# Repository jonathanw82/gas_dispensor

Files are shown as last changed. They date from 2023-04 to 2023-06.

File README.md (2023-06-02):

<div align="center">
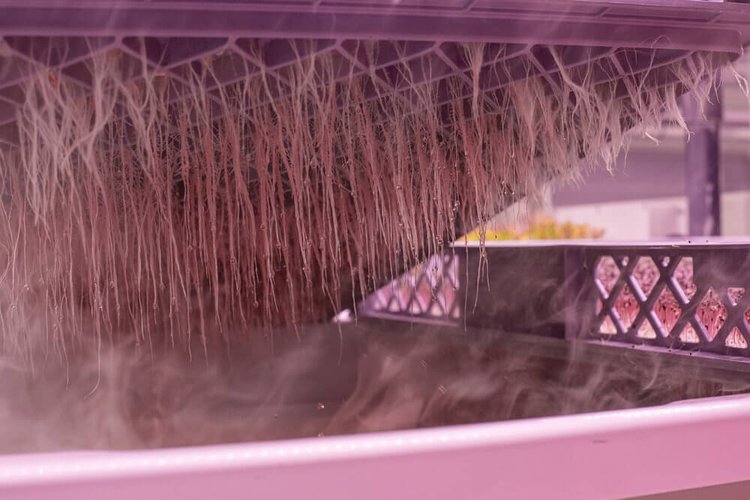
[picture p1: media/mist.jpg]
mist image
   
 </div>

# Overview
This experiment is intended to prove that aeroponics could be less susceptible to [Pythium](https://en.wikipedia.org/wiki/Pythium) a type of root rot, a significant issue for spinach in hydroponic greenhouse production. This test is to confirm that it is possibly due to increased oxygenation with the root zone of the aeroponic system.

The gas dispenser is to reduce the oxygen level in the root zone of an aeroponic growbed by adding nitrogen to bring down the percentage of oxygen.

As can be seen in Fig 1 on average breathable air is made up of oxygen 21%, nitrogen 78.1% and argon and other gasses make only 0.9% of that carbon dioxide makes up 0.04%. 

More information on the composition of air can be found [here.](https://en.wikipedia.org/wiki/Atmosphere_of_Earth)

Therefore increasing the nitrogen level will decrease the oxygen level. Over the growth cycle of some crop this can prove if aeroponics does indeed give the root zone more assess to oxygen and decrease the susceptibility to pythium.

### Fig 1
<div align="center">
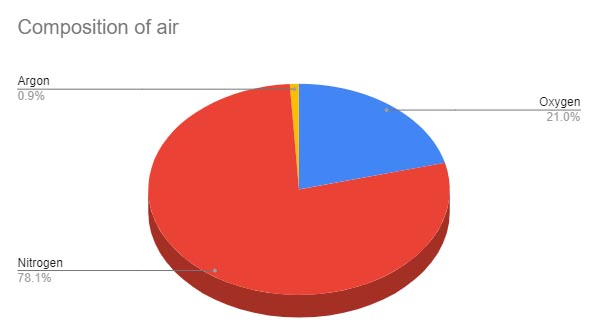
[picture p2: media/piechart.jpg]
piechart
   
 </div>

## Hardware:

* 1 x Arduino Uno wifi rev2
* 1 x Wemos D1 Mini
* 4 x 5v relays
* 1 x 5v PSU
* 1 x Gravity: Electrochemical Oxygen / O2 Sensor (0-100%Vol, I2C) [Here](https://www.dfrobot.com/product-2569.html) (Main 02 sensor) 
* 1 x Gravity: O2 Sensor (Calibrated, I2C & UART) [Here](https://thepihut.com/products/gravity-o2-sensor-calibrated-i2c-uart?variant=41620114866371&currency=GBP&utm_medium=product_sync&utm_source=google&utm_content=sag_organic&utm_campaign=sag_organic&gclid=CjwKCAjw586hBhBrEiwAQYEnHaFBwm7ZAKjgB-vlygECEoYnv8AqbQjYx805CCJuayE0CSrMo6SIVhoCAVIQAvD_BwE) (Safety sensor)
* 1 x Project box
* 5 x Cable glands
* 1 x Cyclinder of nitrogen
* 1 x Bottle regulator with solenoid [Here](https://www.onestopgrowshop.co.uk/pro-leaf-co2-regulator.html)
* 1 x Nitrogen Regulator [Here](https://www.welduk.com/nitrogen-regulator-p64)
* 1 x 1/4 male to 3/8 female BSP adaptor [Here](https://www.air-compressorsdirect.co.uk/bsp-fittings/taper-1-4-male-to-3-8-female-bsp-adaptor)
* 1 x Warning beacon
* 3 x LED's, Red, Green and Amber
* 1 x 4amp 240v MCB
* 1 x 240v to 12v and 5.5v power supply
* 1 x Short piece of din rail 

<br>

| Component               | Consumption        |
| :----------------       | :-----------       |
| Arduino Uno Wifi Rev2   | @ 5v 93 ma         |
| Weemos D1 mini          | @ 5v 70 ma         |
| Twin relay              | @ 5v 40 ma         |
| Single 30amp relay      | @ 5v 20 ma         |
| Oxygen sensor SEN0465   | @ 5v < 5 ma        |
| Oxygen sesnor AA428-210 | @ 5v < 6.5 ma      |
| Warning Beacon          | @ 12v 300 ma       |
| Gas Solenoid            | @ 240v 1 amp       |
| Green status LED        | @ 5v 60 ma         |
| Red status LED          | @ 5v 60 ma         |
| Amber status LED        | @ 5v 60 ma         |
|                         |Total = 1,652.48 amp|

<br>

### Fig 2
<div align="center">
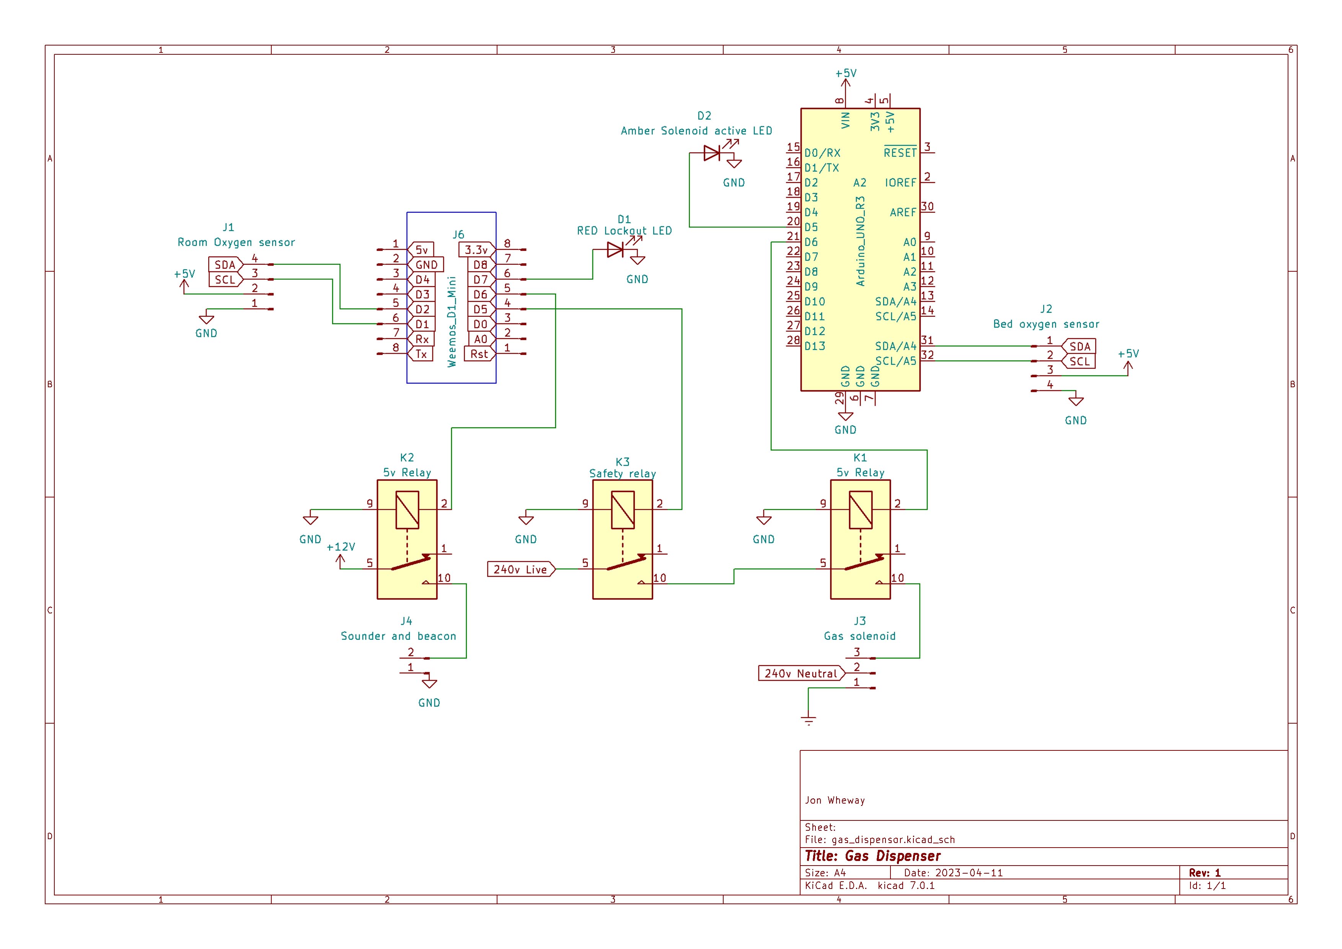
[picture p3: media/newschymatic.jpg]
schymatic
   
 </div>
<br>

## Process:
The safety sensor will read the ambient oxygen level in the room to ascertain if the level of oxygen is within a safe range. Under normal atmospheric pressure conditions, a human normally inhales air that contains 20.9% oxygen, if this falls even by 1 or 2% then it starts to become more laborious and the environment turns hypoxic meaning that oxygen levels are low and could be harmful. [More here](#safety)

If ambient levels are within a safe range the safety relay will energise allowing power throught the dosing relay to energise the solenoid. If 0.0 is reported by the room sensor this is classed as an error. A further 8 samples are taken if they all return 0.0 the error status is reported and the lockout is enguaged and the warning beacon will sound. If during those 8 readings a correct value is retured then the system will continue as normal.

If all is well and the saftey relay is enguaged the bed level oxygen sensor will provide the level of oxygen in the root zone and the dosing solenoid will activate to the specified on off period, lets say 2 seconds on 4 seconds off with a 1 minute pause period to allow the gas to settle and not over shoot the set point. This is also helps to mitigate against the chance of the solenoid from freeing open. This process is repeated to allow more nitrogen into the root zone to bring down the level to the required target. Once the target is met, the system will stop doseing and remain domant until more nitrogen is required and the process starts again. All the while the safety sensor is continuouly checking the oxygen level in the room to keep a safe enviroment.

All the data collected is sent to influxDB for use later, live monitoring can be seen by using mqtt explorer.

### Fig 3
<div align="center">
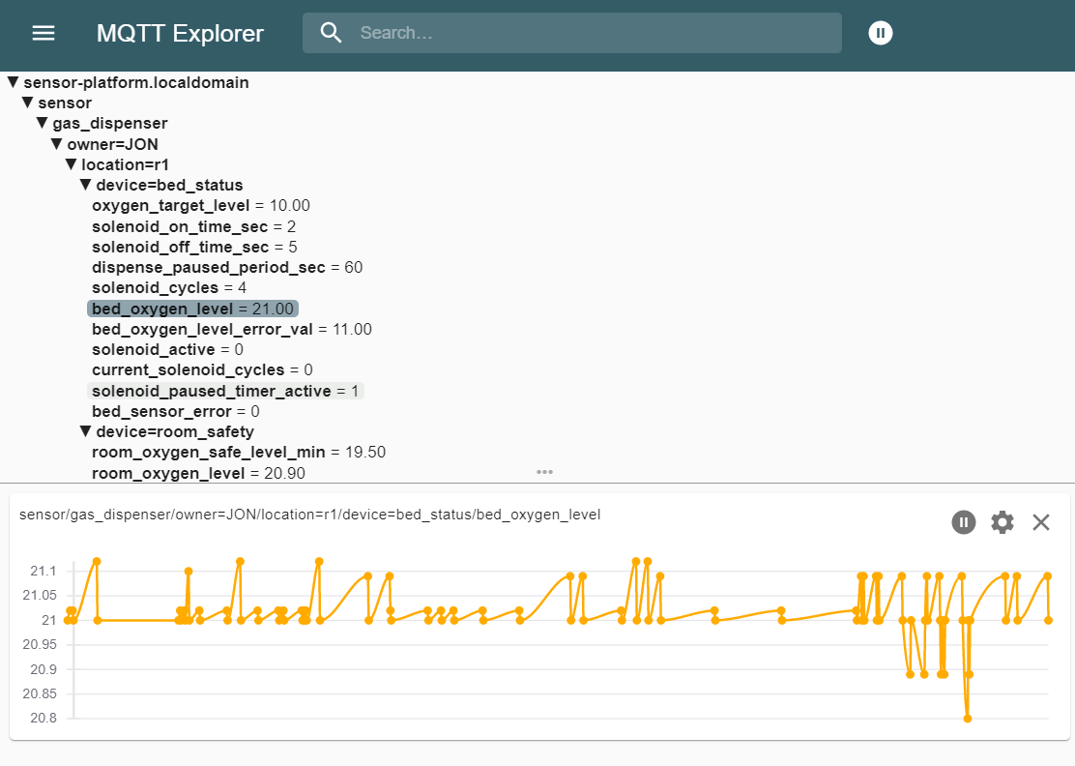
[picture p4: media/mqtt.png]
mqtt
   
 </div>
<br>

## Control commands:
Commands can be sent via mqtt to change certain set points or activate resets.

Sensding this command resets both arduinos.
* gas_dispenser/sub/owner=JON/location=r1/reset

The oxygen target level can be adjusted by sending a number to this command.
* gas_dispenser/sub/owner=JON/location=r1/oxygen_target_level

The solenoid on time can be adjusted by sending a number in seconds.
* gas_dispenser/sub/owner=JON/location=r1/solenoid_on_time_sec

The solenoid off time can be adjusted by sending a number in seconds.
* gas_dispenser/sub/owner=JON/location=r1/solenoid_off_time_sec

The solenoid cycles can be adjusted by sending a number.
* gas_dispenser/sub/owner=JON/location=r1/solenoid_cycles

The solenoid off time can be adjusted by sending a number in seconds.
* gas_dispenser/sub/owner=JON/location=r1/dispense_paused_period_sec

<br>

### Fig 4
<div align="center">
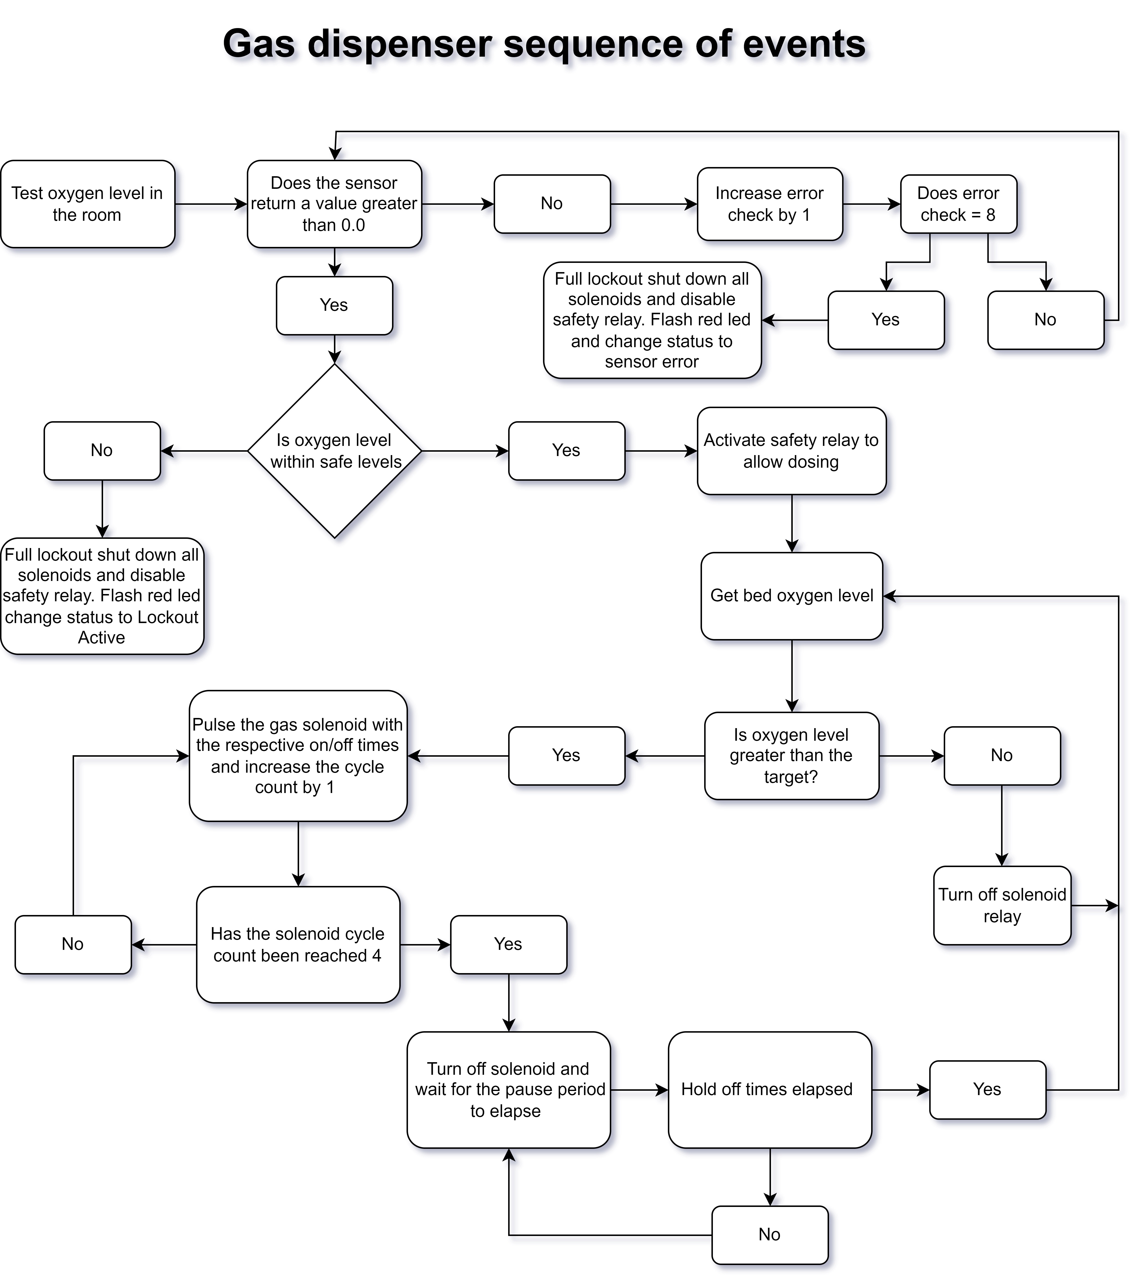
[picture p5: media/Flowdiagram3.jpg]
flowchart3
   
 </div>
<br>

### Fig 5
<div align="center">
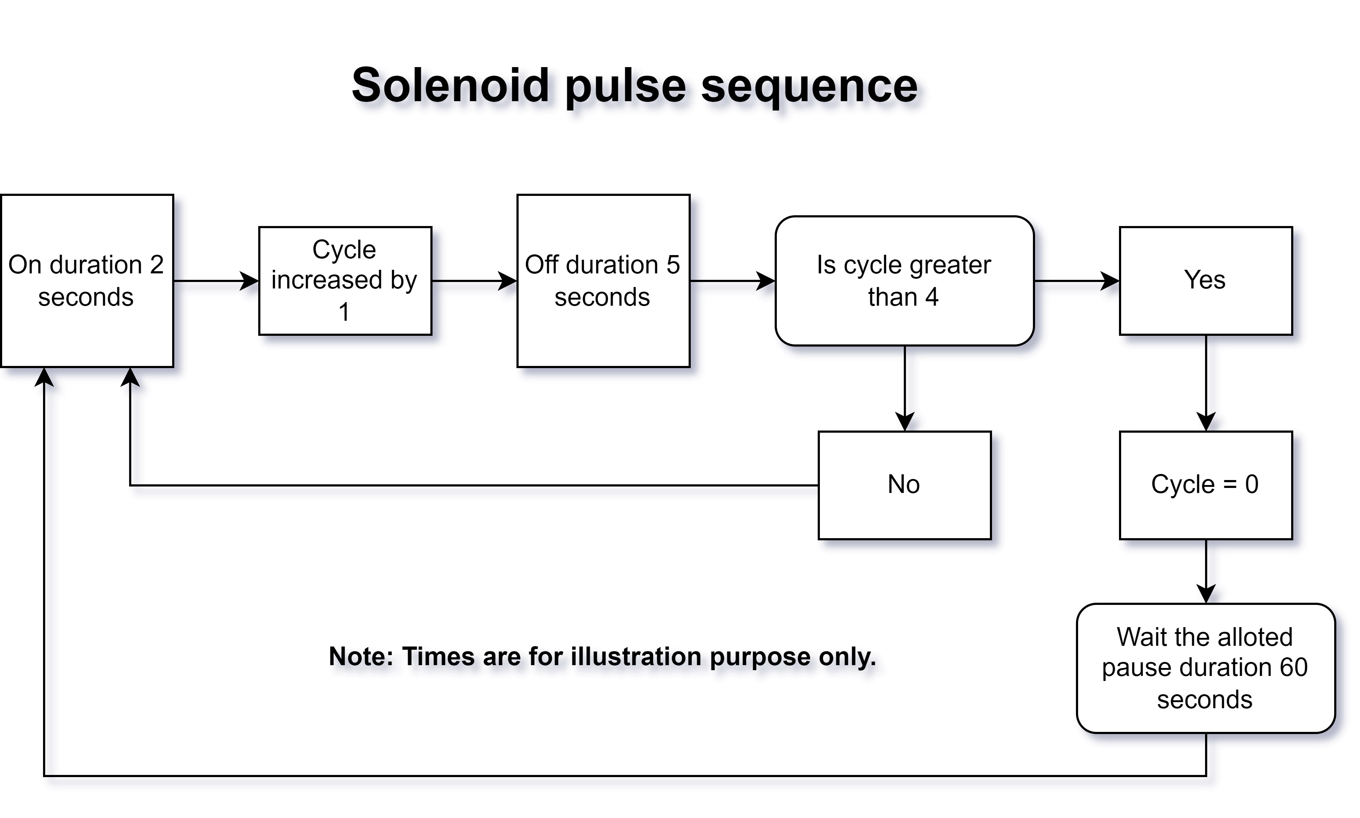
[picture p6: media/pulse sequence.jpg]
pulse sequence
   
 </div>
<br>

## Safety:

Two 02 sensors are used, one in the root zone and another in the room. Unsafe oxygen levels are below 19.50% if this is detected the solenoid will be shut down to prevent any more nitrogen from being pumped into the environment a sounder and strobe will also activate. At this point, the only way for the system to start back up is to be physically reset by means of a power cycle by the operator.

The operator will also ware a personal oxygen safety alarm Fig 6 so if the oxygen in the room does fall below 19.50% the alarm will sound alerting the operator of unsafe working conditions and to exit and vent the room immediately.

### Fig 6
<div align="center">
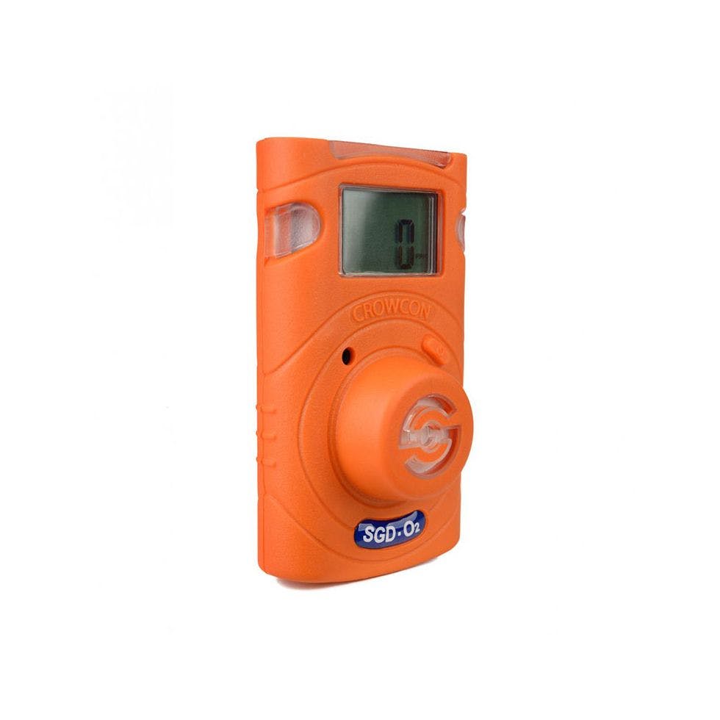
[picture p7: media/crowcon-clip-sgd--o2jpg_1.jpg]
alarm
   
 </div>

<br>

## Notes:

<hr>
https://www.onestopgrowshop.co.uk/pro-leaf-co2-regulator.html

https://www.frontline-safety.co.uk/crowcon-clip-sgd-o2-19-5-23-5?gclid=Cj0KCQjwocShBhCOARIsAFVYq0gQbVtchKTyPnhoyY-E2DVQ6XILTxL77i3xV6OiKG-mPj-r-w2bqaUaArd8EALw_wcB

## refernce notes
https://peoplesafe.co.uk/blogs/safety-when-working-in-low-oxygen-environments/

calibrating the red sensor
https://wiki.dfrobot.com/SKU_SEN0496_Gravity_Electrochemical_Oxygen_Sensor_0_100_I2C

## refernce notes for each oxygen sensor

Gravity: I2C Oxygen / O2 Sensor SEN0465 0~25%Vol [here](https://wiki.dfrobot.com/SKU_SEN0465toSEN0476_Gravity_Gas_Sensor_Calibrated_I2C_UART)

This full-scale oxygen / O2 sensor employs the original AO2 CiTiceL® oxygen sensor 0~100%Vol [here](https://wiki.dfrobot.com/SKU_SEN0496_Gravity_Electrochemical_Oxygen_Sensor_0_100_I2C)

CGA320 bottle connection

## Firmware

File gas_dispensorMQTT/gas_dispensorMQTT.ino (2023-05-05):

/*
  For more information on this code https://github.com/jonathanw82/gas_dispensor
*/
#include <DFRobot_MultiGasSensor.h>
#include <DFRobot_EOxygenSensor.h>
#include <Wire.h>     // I2c enable Lib
#include <avr/wdt.h>  // Watchdog Lib
#include <SPI.h>      // Allow access to serial
#include <PID.h>
#include <WiFiNINA.h>
#include <MQTT.h>
#include <EEPROM.h>
#include <LGcredentials.h>

#define WIFI_NAME ssid
#define WIFI_PASSWORD wifipassword
#define MQTT_HOST mqtt_host_name
#define SUBSCRIBE_PATH "Gas_Dispenser/sub/"
#define DEVICE_NAME "Gas_Dispenser"
#define PUBLISH_PATH "Gas_Dispenser/"
//char PUBLISH_PATH[30] = "sensor/bed-environment/";
char MACADDRESS[18];  // 00:00:00:00:00:00
char LOCATION[5] = "R1";
char OWNER[10] = "owner=JON";
int status = WL_IDLE_STATUS;
MQTTClient mqtt_client;
WiFiClient www_client;

const uint8_t on = HIGH;
const uint8_t off = LOW;
float room_oxygen_level = 0;
float room_oxygen_safe_level_min = 19.50;
bool safety_lockout = false;
bool runaway_lockout = false;
unsigned long runaway_lockout_timer;
unsigned long runaway_lockout_duration_ms = 60000;  // 5 mins
float bed_oxygen_level = 0;
float oxygen_target_level = 10;  // target for oxygen is 10%
int time_period = 30;
float gas_on_time = 0;
float gas_off_time = 0;
float gas_output = 0;
unsigned long prev_Compute_time;
uint16_t pid_compute_interval = 5000;
uint16_t solenoid_pulse_interval = 1000;

//~~~~~~~~~~~~~~~~~~~~~~~~~~~~~~ Decalre control pins  ~~~~~~~~~~~~~~~~~~~~~~~~~~~~~~~~~~~
const uint8_t gas_output_solenoid = LED_BUILTIN;
const uint8_t gas_safety_relay = 2;
const uint8_t warning_beacon = 3;
const uint8_t red_lockout_led = 4;
const uint8_t abmer_solenoid_active_led = 5;
const uint8_t blue_fault_led = 6;

//~~~~~~~~~~~~~~~~~~~~~~~~~~~~~~ Decalre Oxygen sensor  ~~~~~~~~~~~~~~~~~~~~~~~~~~~~~~~~~~

DFRobot_EOxygenSensor_I2C bed_oxygen_sensor(&Wire, 0x70);  // main sensor in the grow bed

#define I2C_COMMUNICATION
DFRobot_GAS_I2C roomSafetyOxygenSensor(&Wire, 0x74);  // safety sensor to shut down output if the oxgen level in the room is unsafe

// input, output, target, P, I, D
PID gasPID(&bed_oxygen_level, &gas_output, &oxygen_target_level, 10, 0.2, 0);  // Decalre the PID classes

//~~~~~~~~~~~~~~~~~~~~~~~~~~~~~~~~~ Watchdog ~~~~~~~~~~~~~~~~~~~~~~~~~~~~~~~~~~~~~~~~~~~~~
void watchdogSetup() {
#ifdef ARDUINO_ARCH_MEGAAVR
  if (RSTCTRL.RSTFR & RSTCTRL_WDRF_bm) {
    Serial.println(F("It was a watchdog reset."));
  }
  RSTCTRL.RSTFR |= RSTCTRL_WDRF_bm;
  wdt_enable(WDT_PERIOD_4KCLK_gc);
#endif
}

//~~~~~~~~~~~~~~~~~~~~~~~~~~~~~~~~~~ Setup ~~~~~~~~~~~~~~~~~~~~~~~~~~~~~~~~~~~~~~~~~~~~~~~
void setup() {
  Serial.begin(9600);
  wifi();
  Wire.begin();
  gasPID.init();  // Initialise Pid for temp and hum
  gasPID.max_out = 100;
  gasPID.min_out = -100;
  get_EEprom();
  pinMode(gas_output_solenoid, OUTPUT);
  digitalWrite(gas_output_solenoid, off);
  pinMode(gas_safety_relay, OUTPUT);
  digitalWrite(gas_safety_relay, off);
  pinMode(warning_beacon, OUTPUT);
  digitalWrite(warning_beacon, off);
  pinMode(red_lockout_led, OUTPUT);
  digitalWrite(red_lockout_led, off);
  pinMode(abmer_solenoid_active_led, OUTPUT);
  digitalWrite(abmer_solenoid_active_led, off);
  pinMode(blue_fault_led, OUTPUT);
  digitalWrite(blue_fault_led, off);

  while (!roomSafetyOxygenSensor.begin()) {
    Serial.println("NO Room Sensor Deivces !");
    delay(1000);
  }
  Serial.println("Room safety oxygen sensor connected successfully !");
  while (!bed_oxygen_sensor.begin()) {
    Serial.println("NO bed sensor Deivces !");
    delay(1000);
  }
  Serial.println("Bed oxygen sensor connected successfully !");
  // if not connected in a timly mannor bring on the error light

  roomSafetyOxygenSensor.changeAcquireMode(roomSafetyOxygenSensor.PASSIVITY);
  watchdogSetup();
}

void loop() {
  wdt_reset();
  maintain_mqtt_connection();
  mqtt_client.loop();
  roomOxygenLevelSafetyCheck();

  static unsigned long publish_timer;
  if (millis() - publish_timer > 5000) {
    publish_timer = millis();
    publishMQTT();
  }

  bool reset_runaway_state_machine = true;
  if (gas_output == -100) {
    reset_runaway_state_machine = false;
  }
  gasSystemRunawayStateCheck(reset_runaway_state_machine);

  if (safety_lockout || runaway_lockout) {
    wdt_reset();
    getRoomOxygenSample();
    digitalWrite(gas_safety_relay, off);
    digitalWrite(red_lockout_led, on);
    digitalWrite(gas_output_solenoid, off);
    digitalWrite(warning_beacon, on);
    return;
  }

  check_time_values();
  time_control_loop();
  if (millis() - prev_Compute_time > pid_compute_interval) {  // Compute every 5 seconds
    prev_Compute_time = millis();
    get_bed_oxygen_reading();
    gasPID.Compute();
  }
}

void getRoomOxygenSample() {
  static unsigned long timer = 0;
  if (millis() - timer < 2000) {
    return;
  }
  timer = millis();
  wdt_reset();
  room_oxygen_level = roomSafetyOxygenSensor.readGasConcentrationPPM();
  wdt_reset();
}

void roomOxygenLevelSafetyCheck() {
  getRoomOxygenSample();
  if (room_oxygen_level <= room_oxygen_safe_level_min) {
    safety_lockout = true;  // the system will have to phsically reset to start up again
    return;
  }
  digitalWrite(gas_safety_relay, on);
  digitalWrite(red_lockout_led, off);
}


float get_bed_oxygen_reading() {
  return bed_oxygen_level = bed_oxygen_sensor.readOxygenConcentration();
}

//~~~~~~~~~~~~~~~~~~~~~~~~~~~~~~~~~ Time values ~~~~~~~~~~~~~~~~~~~~~~~~~~~~~~
void check_time_values() {
  // Convert a negative number to a positive number

  if (gas_output < 0) gas_on_time = (gas_output * time_period) / 100 * -1;  // Temp
  else gas_on_time = (gas_output * time_period) / 100;
  gas_off_time = time_period - gas_on_time;
}

//~~~~~~~~~~~~~~~~~~~~~~~~~~~~~~ Time loop control ~~~~~~~~~~~~~~~~~~~~~~~~~~
void time_control_loop() {
  static unsigned long time_loop_start = 0;

  if (millis() - time_loop_start > (time_period * 1000)) {
    time_loop_start = millis();
  }

  if (millis() - time_loop_start < (gas_on_time * 1000)) {
    if (gas_output > 0) {
      digitalWrite(gas_output_solenoid, off);
      digitalWrite(abmer_solenoid_active_led, off);
    } else {
      activate_solenoid();  // increases nitrogen level
    }
  } else {
    digitalWrite(gas_output_solenoid, off);
  }
}

void activate_solenoid() {
  static unsigned long solenoid_wait_timer;
  if (millis() - solenoid_wait_timer < solenoid_pulse_interval) {
    return;
  }
  solenoid_wait_timer = millis();
  digitalWrite(gas_output_solenoid, !digitalRead(gas_output_solenoid));  // pulse the gas_output solenoid to avoid freezing
  digitalWrite(abmer_solenoid_active_led, !digitalRead(abmer_solenoid_active_led));
}

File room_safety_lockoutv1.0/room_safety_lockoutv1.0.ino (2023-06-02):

#include <ESP8266WiFi.h>
#include <DFRobot_MultiGasSensor.h>
#include <MQTT.h>
#include <OneWire.h>
#include <LGcredentials.h>

#define WIFI_NAME ssid
#define WIFI_PASSWORD wifipassword
#define MQTT_HOST mqtt_host_name
#define SUBSCRIBE_PATH "gas_dispenser/sub/"
#define DEVICE_NAME "Room_oxygen_safety_level_sensor"
char PUBLISH_PATH[40] = "sensor/gas_dispenser/";
char MACADDRESS[20];  // 00:00:00:00:00:00
char LOCATION[15] = "location=r1";
char OWNER[15] = "owner=JON";
int status = WL_IDLE_STATUS;
MQTTClient mqtt_client;
WiFiClient espClient;

const uint8_t on = LOW;
const uint8_t off = HIGH;
float room_oxygen_level = 0;
float room_oxygen_safe_level_min = 19.50;
bool safety_lockout = false;
bool sensor_fault = false;

const uint8_t gas_safety_relay = D5;
const uint8_t warning_beacon = D6;
const uint8_t red_lockout_led = D7;


#define I2C_COMMUNICATION
DFRobot_GAS_I2C roomSafetyOxygenSensor(&Wire, 0x74);  // safety sensor to shut down output if the oxgen level in the room is unsafe

void setup() {
  Serial.begin(9600);
  setup_wifi();
  pinMode(gas_safety_relay, OUTPUT);
  digitalWrite(gas_safety_relay, off);
  pinMode(warning_beacon, OUTPUT);
  digitalWrite(warning_beacon, off);
  pinMode(red_lockout_led, OUTPUT);
  digitalWrite(red_lockout_led, off);

  while (!roomSafetyOxygenSensor.begin()) {
    Serial.println("NO Deivces !");
    delay(1000);
  }
  Serial.println("Room safety oxygen sensor connected successfully !");
  roomSafetyOxygenSensor.changeAcquireMode(roomSafetyOxygenSensor.PASSIVITY);
}

void loop() {
  maintain_wifi_connection();
  if(WiFi.status() == WL_CONNECTED){
    maintain_mqtt_connection();
  }
  mqtt_client.loop();
  roomOxygenLevelSafetyCheck();
  publishMQTT();

  if (safety_lockout) {
    getRoomOxygenSample();
    lockoutLed();
    digitalWrite(gas_safety_relay, off);
    digitalWrite(warning_beacon, on);
    return;
  }
}

void getRoomOxygenSample() {
  static unsigned long timer = 0;
  static uint8_t error_check = 0;
  static uint8_t error_check_max = 8;
  static float check_oxygen_reading = 0;

  if (millis() - timer < 2000) {
    return;
  }
  timer = millis();
  check_oxygen_reading = roomSafetyOxygenSensor.readGasConcentrationPPM();

  if (error_check == error_check_max) {
    Serial.println("** Room safety oxygen sensor fault ! **");
    safety_lockout = true;  // the system will have to phsically reset to start up again
    sensor_fault = true;
    return;
  }

  if (check_oxygen_reading == 0.0) {
    error_check++;
    Serial.print("error check = ");
    Serial.println(error_check);
  } else {
    error_check = 0;
    room_oxygen_level = check_oxygen_reading;
  }
}

void roomOxygenLevelSafetyCheck() {
  getRoomOxygenSample();
  if (room_oxygen_level <= room_oxygen_safe_level_min) {
    safety_lockout = true;  // the system will have to phsically reset to start up again
    return;
  }
  if (!safety_lockout) {
    digitalWrite(gas_safety_relay, on);
    digitalWrite(red_lockout_led, LOW);
    digitalWrite(warning_beacon, off);
  }
}

void lockoutLed() {
  static unsigned long timer;
  if (millis() - timer < 1000) {
    return;
  }
  timer = millis();
  digitalWrite(red_lockout_led, !digitalRead(red_lockout_led));
}

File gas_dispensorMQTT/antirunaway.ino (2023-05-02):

int second = 0;

void timeclock() {
  static unsigned long time = 0;
  if (millis() - time > 1000) {
    time = millis();
    second++;
    Serial.println(second);
  }
}

void set_runaway_lockout() {
  /*
   Check if the runaway lockout is true if not set it true and start the timer
  */
  if (runaway_lockout) {
    return;
  }
  Serial.println(F("Setting runaaway lockout"));
  runaway_lockout = true;
  runaway_lockout_timer = millis();
}

void manage_runaway_lockout() {
  /*
   If the runaway lockout is true check the timer if it elaspes set runaway lockout to false
  */
  if (!runaway_lockout) {
    return;
  }
  if (millis() - runaway_lockout_timer > runaway_lockout_duration_ms) {
    Serial.println(F("Unsetting runaaway lockout"));
    runaway_lockout = false;
  }
}

void gasSystemRunawayStateCheck(bool reset) {
  static float gassample_average = 0;
  static float gas_sample1 = 0;
  static float gas_sample2 = 0;
  static float gas_sample3 = 0;
  static uint8_t checkGas = 0;
  static bool getsample1 = true;
  static bool getsample2 = true;
  static bool getsample3 = true;
  static unsigned long timer = 0;
  static unsigned long timer1 = 0;
  static uint8_t step = 0;

  manage_runaway_lockout();

  if (reset) {
    //
    getsample1 = true;
    getsample2 = true;
    getsample3 = true;
    checkGas = 0;
    step = 0;
    return;
  }

  switch (step) {
    case 0:
      if (getsample1) {
        gas_sample1 = get_bed_oxygen_reading();
        getsample1 = false;
        Serial.println(F("Got sample 1"));
        timer = millis();
        wdt_reset();
      }
      if (millis() - timer < 5000) {
        return;
      }
      timer = millis();
      if (getsample2) {
        gas_sample2 = get_bed_oxygen_reading();
        getsample2 = false;
        Serial.println(F("Got sample 2"));
        timer1 = millis();
        wdt_reset();
      }
      if (millis() - timer1 < 5000) {
        return;
      }
      timer1 = millis();
      if (getsample3) {
        gas_sample3 = get_bed_oxygen_reading();
        getsample3 = false;
        Serial.println(F("Got sample 3"));
        step = 1;
        wdt_reset();
      }
      break;
    case 1:
      if (millis() - timer < 5000) {  // wait 30 seconds
        return;
      }
      timer = millis();
      Serial.println(F("Timer elapsed"));
      getsample1 = false;
      getsample2 = false;
      getsample3 = false;
      gassample_average = (gas_sample1 + gas_sample2 + gas_sample3) / 3;
      Serial.print(F("This is the average sample = "));
      Serial.println(gassample_average);
      step = 2;
      wdt_reset();
      break;
    case 2:
      Serial.print("step is now =");
      Serial.println(step);
      if (get_bed_oxygen_reading() < gassample_average - .3) {
        wdt_reset();
        Serial.print("Gas moving in the right direction");
        checkGas = 0;
        step = 0;
      } else {
        step = 3;
      }
      break;
    case 3:
      static float low = gassample_average - .1;
      static float high = gassample_average + .1;
      Serial.print(F("Low = "));
      Serial.println(low);
      Serial.print(F("gas value = "));
      Serial.println(get_bed_oxygen_reading());
      Serial.print(F("High = "));
      Serial.println(high);
      if (low <= get_bed_oxygen_reading() && get_bed_oxygen_reading() <= high) {
        checkGas++;
        Serial.print(F("Nothing changed increse gas by 1 new value = "));
        Serial.println(checkGas);
        wdt_reset();
      }
      if (checkGas == 4) {
        // here set runaway lockout
        set_runaway_lockout();
        checkGas = 0;
      }
      getsample1 = true;
      getsample2 = true;
      getsample3 = true;
      step = 0;
      break;
  }
}

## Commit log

2023-04-10 added another sensor for safety
2023-04-24 added safety relay and leds
2023-04-28 addede the sensor begins
2023-05-02 added flow chart
2023-05-02 added flow chart2
2023-05-04 moved room safety sensor to a separate arduino D1 mini and the dosing to uno wifi
2023-05-05 added schmatic
    [gas_dispensor.kicad_pcb, gas_dispensor.kicad_sch]
2023-05-05 added new schymatic
    [gas_dispensor.kicad_sch]
2023-05-06 refactured the relay control
    [gas_dispensor.kicad_sch]
2023-05-09 added error checking to the dispensing arduino
